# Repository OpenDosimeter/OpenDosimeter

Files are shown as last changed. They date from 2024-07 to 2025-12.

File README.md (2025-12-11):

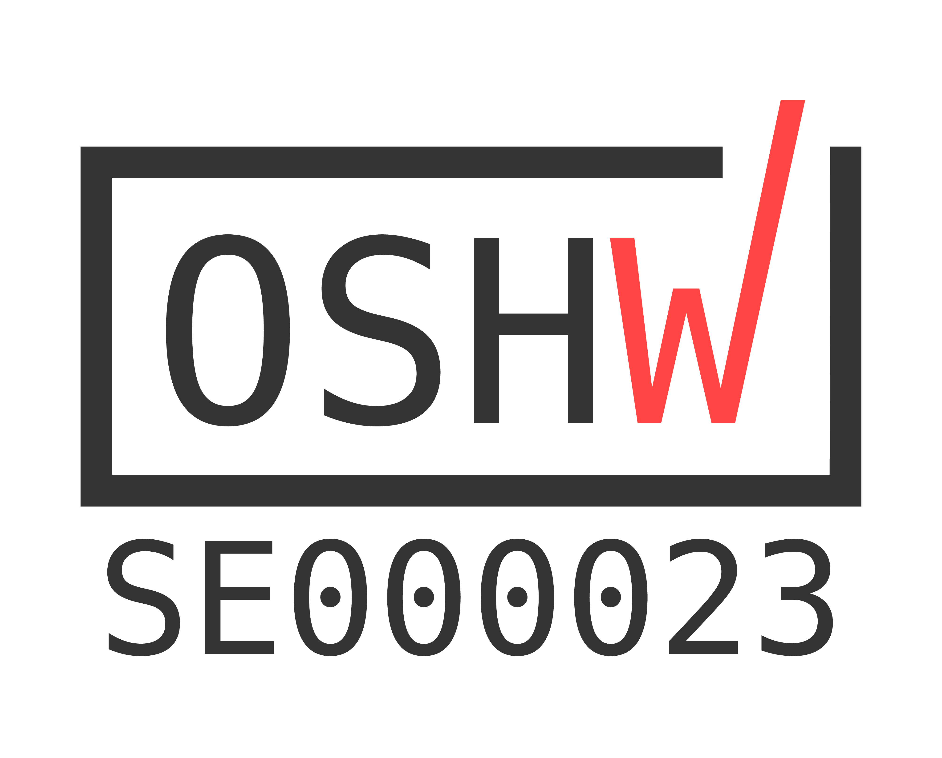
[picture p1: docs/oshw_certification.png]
# OpenDosimeter 

Our open-source hardware and software dosimeter offers an afordable solution for real-time, self-monitored X-ray radiation exposure. With a total component cost of roughly $90, this device provides an accessible option for radiation monitoring to promote broad access to radiation safety. This project is a derivative of the [Open Gamma Detector](https://github.com/OpenGammaProject/Open-Gamma-Detector), with the main new feature being the effective dose calculations (in Sieverts) converted from the detected X-ray spectrum.


<br>
      <blockquote>
        <strong>SAFETY DISCLAIMER:</strong> This is a research project; builders and users assume full responsibility for verifying the accuracy and reliability of measurements obtained from the dosimeters they build. Always follow proper radiation safety protocols and consult with qualified professionals when dealing with radiation exposure.
      </blockquote>
<br clear="both">

<br>

**As of December 1, 2025**, the paper on  OpenDosimeter has been peer reviewed and published in _Communications Engineering_:

<blockquote>

N. Ger, A. Ku, J. Lopez, N. R. Bennett, J. Wang, G. Ateka, E. Anyenda, M. Rosezky, P. Kilavi, A. S. Wang, & K. Shaker, [*"OpenDosimeter: Open hardware personal X-ray dosimeter"*](https://doi.org/10.1038/s44172-025-00540-0) _Commun Eng_ 4, 207 (2025)

</blockquote>

Please cite the paper above if you want to reference the OpenDosimeter project.

## Key Features 

Cost Breakdown

- **Open Design:** Hardware and software designs are fully open-source, enabling reproducibility and customization
- **Affordable:** Total cost ~$90, see [here](https://github.com/OpenDosimeter/OpenDosimeter/tree/main/hardware#table-of-materials) and cost breakdown →
- **Compact:** 73 mm x 42 mm x 23 mm (with the case)
- **Programmable:** Drag and drop firmware files
- **Battery powered:** Current version has a capacity of up to 20 hours per full charge (<70 mA @ at 3.7V, 1200 mAh battery)
- **Accuracy:** Currently reliable between around **0.1 µSv/h to 1 mSv/h** (±25% accuracy) in the [photon counting](https://github.com/OpenDosimeter/OpenDosimeter/blob/main/README.md#working-principle) range
- **Buzzer:** Built in buzzer allows for optional audible warnings when dose rate exceeds predefined limit (default set to 5 µSv/h)
- **Calibratable:** Using Am-241 from any household ionization smoke detector for spectral/dose calibration
- **Real-time:** Direct feedback on radiation exposure, compared to passive dosimeters (e.g., OSL or TLD badges) requiring external readout
- **Logging:** The last 10 hours of dose values are stored on the device; extracted through USB connection and our web interface [here](https://opendosimeter.org/#dataLog)
<br clear="right">

## How to Make One 
**This repository has everything you need to create your own OpenDosimeter:** 

**[Case](https://github.com/OpenDosimeter/OpenDosimeter/tree/main/case):** Use this directory to 3D print the case. It contains two sets of ``.stl`` files that can be downloaded to print top and bottom components for a case with and without a belt clip. 

**[Docs](https://github.com/OpenDosimeter/OpenDosimeter/tree/main/docs):** This is where you can find the reference images used throughout this repository. 

**[Software](https://github.com/OpenDosimeter/OpenDosimeter/tree/main/software):** The software directory has everything you need to program your device, whether you are just looking to download the software with default settings or looking to modify the firmware and make changes to the sketch.  After programming your device, you will be guided through local calibration of your device and an overview of how to use it. 

**[Hardware](https://github.com/OpenDosimeter/OpenDosimeter/tree/main/hardware):** Check out the hardware directory to see the OpenDosimeter board layout in EasyEDA and instructions for ordering it using JLCPCB. This directory contains a breakdown of each component required to assemble the hardware with prices and links to order parts. Furthermore, this is where you can find instructions to assemble your device. 
Additionally, if you prefer to order directly from the PCB manufacturer, you can download the gerber file also located in the ``hardware`` directory or at the [OpenDosimeter Kitspace page](https://kitspace.org/OpenDosimeter/OpenDosimeter).

**[@OpenDosimeter](https://www.youtube.com/channel/UCCUE-LeyRK8Y6H67ti1gdNA):** Finally, head over to our YouTube channel for instructional manuals on ordering the PCB, assembling, programming, and calibrating the device.

## Working Principle 
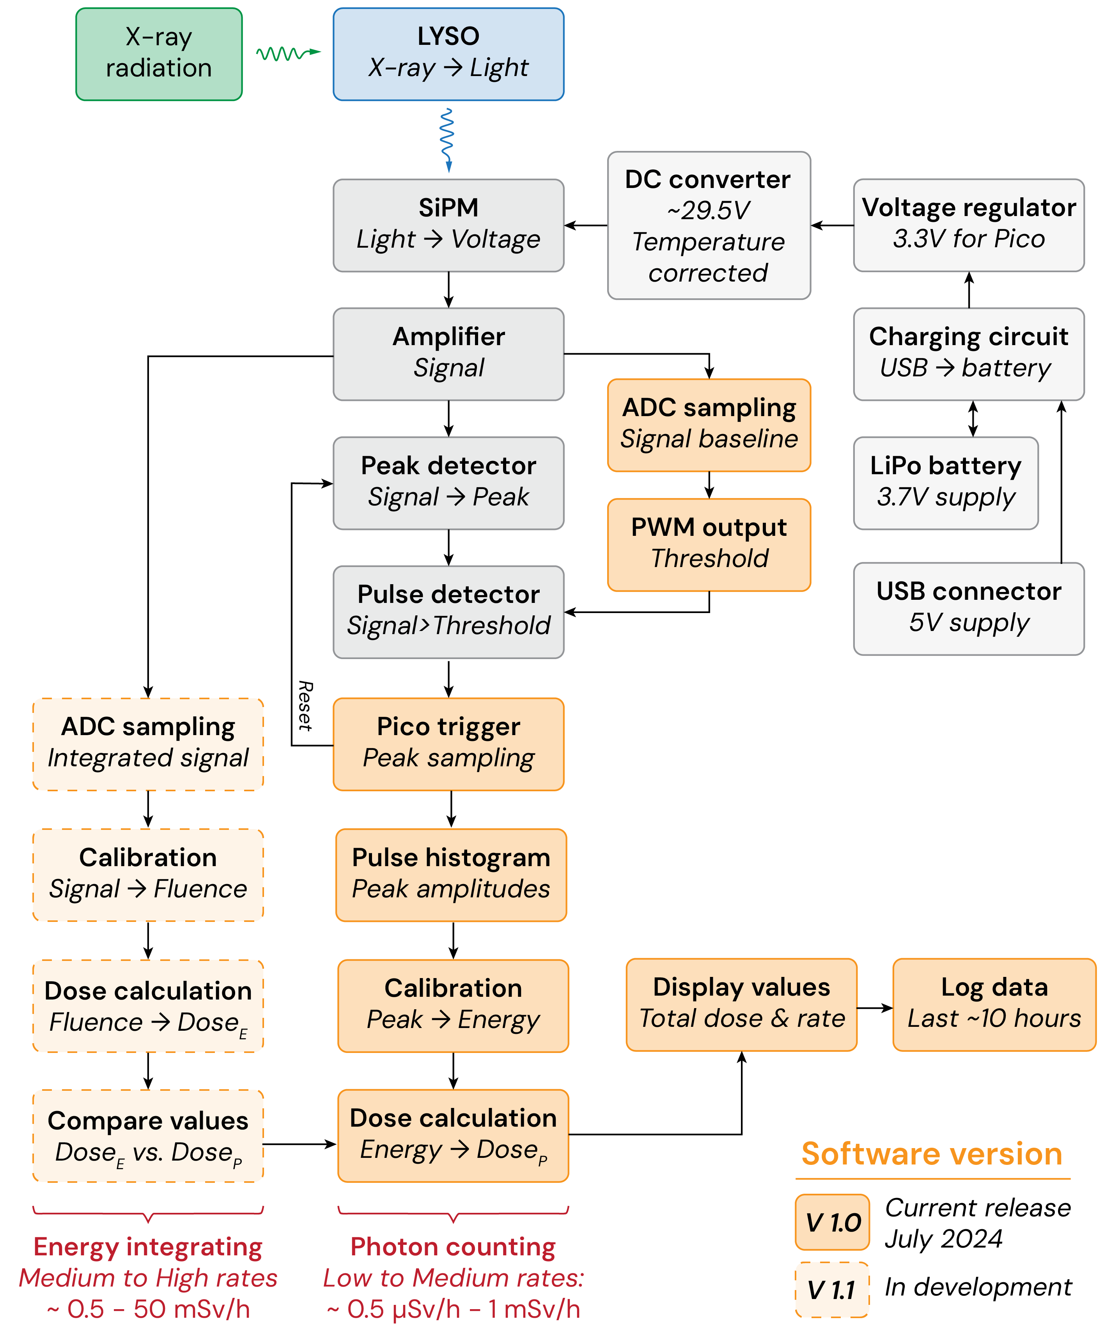
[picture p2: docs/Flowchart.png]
Flowchart of device principle


The flow chart below illustrates the operation, using grey boxes to represent hardware components and orange boxes to indicate software functionality (inspired by the [Open Gamma Detector flowchart](https://github.com/OpenGammaProject/Open-Gamma-Detector/tree/main?tab=readme-ov-file#working-principle), demonstrating the similarity of the underlying design)

The current software (``V.1.0``) converts X-ray photons to dose using a ***photon-counting*** principle (suitable for low to medium dose rates) 

An ***energy-integrating*** parallel component (suitable for medium to high dose rates) is under development for an upcoming software upgrade (``V.1.1``)

<br clear="right">

## Troubleshooting and FAQ
Refer to [REFERENCE.md](https://github.com/OpenDosimeter/OpenDosimeter/blob/main/REFERENCE.md) for troubleshooting support and guidance in debugging

## Future Improvements
1. The current power switch on the OpenDosimeter board is fragile and sometimes breaks. Future iterations of the hardware should replace for a more durable model
2. The power consumption of the current version is quite high (up to 70 mA @ 3.7 V), as it hasn't been optimized for power efficiency. Future hardware and software improvements should be able to improve the power efficiency by at least 2x (i.e., up to 40 hours battery life with a 1200 mAh capacity LiPo).
3. In order to make an even more integrated and compact design, the RP2040 chip from the Raspberry Pi Pico could be incorporated into the OpenDosimeter board 

## Project Team
Many people have contributed to the realization of this project so far:
- Kian Shaker (Stanford University) **[Project lead]**
- Alice Ku (Stanford University)
- Jasmyn Lopez (Stanford University)
- Enoch Anyenda (University of Nairobi)
- Norah Ger (Mama Lucy Kibaki Hospital, Nairobi)
- Grace Ateka (Kenya Bureau of Standards)
- Jia Wang (Stanford University)
- Robert Bennett (Stanford University)
- Adam Wang (Stanford University)
- Matthias Rosezky (https://nuclearphoenix.xyz/)

## Contributing
The OpenDosimeter is a living project and we invite people to contribute to future development!

Want to contribute as a developer? Reach out to [Kian Shaker](https://www.kth.se/profile/kiansd?l=en) (or send an e-mail to opendosimeter@gmail.com)

### Submitting Issues and Suggestions

If you encounter any problems, have questions, or want to suggest improvements:

1. Go to our [Issues page](https://github.com/OpenDosimeter/OpenDosimeter/issues).
2. Click on "New Issue".
4. Provide as much detail as possible about your issue or suggestion.

*Note:* You'll need a GitHub account to submit issues. Another option to leave feedback is to contact us through opendosimeter@gmail.com.

## License

The OpenDosimeter project is released under the GNU General Public License v3.0 (GPL3). This means you're free to use, modify, and distribute the project for any purpose, including commercial applications. However, if you distribute software based on OpenDosimeter, you must make your source code available under the same GPL3 license. This ensures that improvements remain accessible to the community. We encourage innovation and commercial development, as we believe this can lead to wider adoption and further enhancements in radiation safety technology. For the full license text, see the [LICENSE](https://github.com/OpenDosimeter/OpenDosimeter/tree/main?tab=GPL-3.0-1-ov-file) tab in our repository.

## Citation

If your project references OpenDosimeter, or if you use it as a basis for your next cool project, please cite the paper:
<blockquote>

N. Ger, A. Ku, J. Lopez, N. R. Bennett, J. Wang, G. Ateka, E. Anyenda, M. Rosezky, P. Kilavi, A. S. Wang, & K. Shaker, [*"OpenDosimeter: Open hardware personal X-ray dosimeter"*](https://doi.org/10.1038/s44172-025-00540-0) _Commun Eng_ 4, 207 (2025)

</blockquote>

Or directly use the BibTex entry below:

```bibtex
@article{ger2025opendosimeter,
  title={OpenDosimeter: Open hardware personal X-ray dosimeter},
  author={Ger, Norah and Ku, Alice and Lopez, Jasmyn and Bennett, N Robert and Wang, Jia and Ateka, Grace and Anyenda, Enoch and Rosezky, Matthias and Kilavi, Pamela and Wang, Adam S and others},
  journal={Communications Engineering},
  volume={4},
  number={1},
  pages={207},
  year={2025},
  publisher={Nature Publishing Group UK London}
} 

```

## Acknowledgements
_Inspiration:_ The basis for our hardware and software is the fantastic [Open Gamma Detector](https://github.com/OpenGammaProject/Open-Gamma-Detector/tree/main) project, check it out! Much of its detailed documentation is relevant to the OpenDosimeter as well (SiPM behavior, X-ray counting concept etc.)

_Funding support:_ King Center on Global Development at Stanford University, Knut and Alice Wallenberg Foundation (PI: Kian Shaker)

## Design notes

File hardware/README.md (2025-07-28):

# Hardware
Our design leverages the custom OpenDosimeter board with external components including a scintillation crystal (LYSO) coupled to a silicon photomultiplier (SiPM) for X-ray detection, and a Raspberry Pico as for the computation. The board and its components for assembly can also be viewed on [Kitspace](https://kitspace.org/OpenDosimeter/OpenDosimeter). The figure below shows the key features of the OpenDosimeter board. 
<div align=center>
board-overview
</div>

## Components

### OpenDosimeter PCB
Follow these steps to order the OpenDosimeter board (see video instructions below):
1. **Download Files:** download the following files located in this folder
    - [OpenDosimeter_PCB_EasyEDA.json](https://github.com/OpenDosimeter/OpenDosimeter/blob/main/hardware/OpenDosimeter_PCB_EasyEDA.json)
    - [OpenDosimeter_SCH_EasyEDA.json](https://github.com/OpenDosimeter/OpenDosimeter/blob/main/hardware/OpenDosimeter_SCH_EasyEDA.json)
2. **Open in EasyEDA**
    - Go to www.easyeda.com
    - Create an account (or log in if you have one already)
    - Click ``Design Online``
    - Click ``Std Edition``
    - Click ``New Project`` and give it a title
    - Drag and drop both the ``PCB`` and ``SCH`` files into EasyEDA

      | Schematic |Image of Schematic File|
      |---------------------------------------------|--------------------------------------------------------------------------------------|
      | **PCB** |Image of PCB File |

    - ``File`` --> ``Save`` or ``CMD + s`` to save both files to the project you created
    - On the PCB file, click ``Fabrication`` --> ``One Click Order PCB/SMT`` --> ``Yes, Check DCR`` --> ``One Click Order`` --> ``OK``
3. **Open in JLCPCB**
    - Once redirected to JLCPCB, log in or create an account
    - Choose quantity of PCB
    - Recommended: ``Select LeadFree HSL``
    - Select ``PCB Assembly``
    - ``Confirm`` --> ``Next`` --> ``Next`` --> ``OK``
    - Select a product description from drop down
    - Add to cart and checkout
  
**A complete video tutorial for ordering the OpenDosimeter Board is on our YouTube**
<div align="center">
<a href="https://youtu.be/UWabvXynp9I" target="_blank">
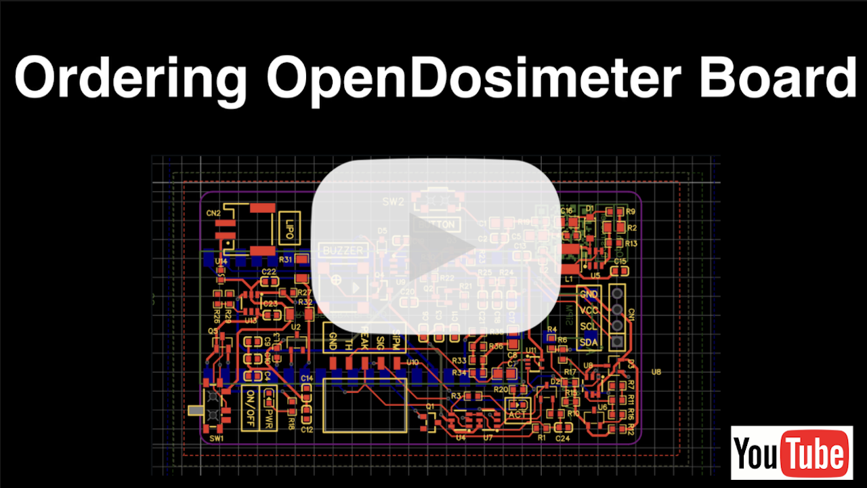
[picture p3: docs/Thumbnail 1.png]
Ordering OpenDosimeter Board Thumbnail
    
</a>
</div>
</br>

### 3D Printed Case 
We have designed a 3D-printable case for the OpenDosimeter. Each case has two parts, a top and bottom. The ``.stl`` files can be found in the [case](https://github.com/OpenDosimeter/OpenDosimeter/tree/main/case) folder.

### Table of Materials
Here are all of the required components and tools for assembly. Also included is the purpose, specification details, cost, and links to purchase each component. 
| Component            | Purpose  | Specification| Cost (USD) | Where to buy (example) |
|------------------------|--------|------------------|------------|---------|
|OpenDosimeter PCB| Main Board  |Custom PCB, see instructions above | $20 |Directly from PCB manufacturer |
|Battery  | Power |LiPo protected battery, ideally >1200 mAh, size around 34mm x 62mm x 5mm | $10 |[1200 mAh Lipo battery](https://www.digikey.com/en/products/detail/adafruit-industries-llc/258/5054544) |
|Display| Displaying dose values to user |128x64 pixels, I2C, SSD1306 | $5 | [Amazon, 128x64 pixels, I2C, SSD1306](https://www.amazon.com/Teyleten-Robot-Display-SSD1306-Raspberry/dp/B0CN373JF4/ref=sr_1_4?crid=2FMQS7B2IFQAD&dib=eyJ2IjoiMSJ9.l-FK2pxw8wWhZ_wtkFb4O1fyrXLIhGQ52dk_-yA7h6FWtEW-CW5RA7_9w5hhpIE9lSkkBIurGV3JAYvQS695jjQR0VVPaO92fd4QVHkD4CTCp4bQsF8CrU8NM0aMPuOZ8RjYMbesVbpG_UDMbMGqyALbXdphIb0nHzBxKLcVF0Pm0UNgyMb1CITVfuh6bqspsPWljCJVLda51Ct931b4NpiFFhTkOtDTzaaWjYwOTCTaZgTjvpziUI1kPpnvJCXBBrgzoC6xlvPtjO4YGGF54xkeJpWnkoouL7rm1iE_GsA.JpSEJVJP5Itir15xcqstihVBHkHDpMhWXXJUSeBi6w4&dib_tag=se&keywords=i2c+128x64+oled+display&qid=1717603122&s=electronics&sprefix=i2c+128x64+oled+sipl%2Celectronics%2C134&sr=1-4) |
|Raspberry Pi Pico| Microcontroller for programming |Regular version with no headers | $4 | [Raspberry Pico](https://www.digikey.com/en/products/detail/raspberry-pi/SC0915/13684020) |
|SiPM| Visible light sensor |6 mm model (MICROFC-60035-SMT-TR) | $33 | [MICROFC-60035-SMT-TR onsemi](https://www.digikey.com/en/products/detail/onsemi/MICROFC-60035-SMT-TR/9742618) |
|LYSO crystal| X-ray to visible light conversion|5x5x1 mm| $30 | [LYSO Ce, 5 x 5 x 1mm](https://www.epic-scintillator.com/LYSO-scintillator-5x5x1mm) |
|Plastic tweezer| Handling LYSO and SiPM | Plastic to prevent scratching the components| $5 |[Amazon, Electronic Repair Plastic Tweezers](https://www.amazon.com/Auniwaig-Anti-static-Tweezers-Precision-Electronics/dp/B08V4BF99K/ref=sr_1_12?crid=2P40DUMKMZHT0&dib=eyJ2IjoiMSJ9.5iYaL1v0I09-iIDQSI0il9h9dCchGEMT1_R94GDH6QmGBH9JFVbAaTAhQZnx0XBo4cjV3EEqDrwTKModIGqUoZWvEqlQyNpFlKvh4ELaqovPHcoU8QCtQ_gAPJ3ZQqBBykfEOf3ee_Jy_4Cu1DA4cSwaO0_pREw9jqP76LslU0dONBOJbGBz6dSRFpDfedrx9rXWLsOMbWLiBONTW1WC0Ly0xX2P2gjgEt74SLqEWsFbY5vmGJeui-m0vcTuJ7wPjrXGSxMzvf9YKbVLzJ0jwkunz39TJtpU8bXlPIO1iSg.wfmLhkznWWSroapnGolqC6t9x1-rZ5mUHo_qM8KZED4&dib_tag=se&keywords=plastic+tweezer+1+pc&qid=1722446225&refinements=p_36%3A-600&rnid=1243644011&sprefix=plastic+tweezer+1+pc%2Caps%2C127&sr=8-12) |
|Electrical Tape| Light sealing of X-ray sensor assembly (SiPM + LYSO) |Black color to efficiently absorb light| $5 |[Amazon, 3/4 Inch Black Electrical Tape ](https://www.amazon.com/Scotch-Super-33-Electrical-carton/dp/B0000AZ9HG/ref=sr_1_3?crid=379MWXWL4Y0R4&dib=eyJ2IjoiMSJ9.XvYh8n8zmezRYWLAeSMp20zS9aMZ_OkZg9vVBnTuU9GBnum6MaLk_FPOJdiiIQndOT6PMejF4weVSVKhDYIE3xq4anvIYIb2bUix0Xf1IJWaM_yuLf7KJLssxgNuyph5Qr31Q8kyOHiXkHE_QoVhGvJzU42l153y9bNqDpVcdg1LXhe9vM8SUbilLvBktT7x3NhoBBvg5GYRCd9G_OwcpAwru3oxciV83fxZaOs_FNA.jo3fPo-i_RRH7EV2clOFCC7W_iUatKs2lCPoXZ7GGuU&dib_tag=se&keywords=electrical+tape+black+3M&qid=1722446293&sprefix=electrical+tape+black+3m%2Caps%2C133&sr=8-3) |
|Aluminum Tape| Light sealing of X-ray sensor assembly (SiPM + LYSO) | Up to 0.1mm thickness to avoid absorbing X-rays | $19 |[Amazon, Aluminum Foil Tape(3M)](https://www.amazon.com/3M-Foil-Tape-3381-Silver/dp/B00A7I5L86/ref=sr_1_4?crid=3FZZ6HXVJFKJW&dib=eyJ2IjoiMSJ9.8g7E604QbHpwyZvpiHS3KOL4D3rbTgkJXTTxyiqD9h9b-tUnIXUthRJ0kzFq5Y0kKPXasQMRFyWgzRdT74c3A0QlN1IbgHV3P2SP6Lm4cNlWMsj0mbBnfrKRNlUb_2VNj8dCcybmoFVXx98mwtjPjzYzJFfLs8Ut27cfT1oYEoi0NeQUm26s7w9ase0wYRub1rl0tQPrTFYCIdzNUsw3XmRI0fHvdR4uIouX2Y2r9mk.iRudZFUJZVLtJbsEUs6dUpkbcNRu_nmlgzl6Sg9rv3g&dib_tag=se&keywords=aluminum+tape+3m&qid=1722446481&sprefix=aluminum+tape+3m%2Caps%2C134&sr=8-4) |
|Optical Couplant | Improving light coupling and adhesion between LYSO crystal and the SiPM  | Should be viscous enough to apply easily, but any will do | $33 | [Amazon, MOLYKOTE 4 Electrical Insulating Compound](https://www.amazon.com/Dow-Corning-Electrical-Insulating-Compound/dp/B0195UWAHG/ref=sr_1_1?crid=1FDS4YSQBHPVO&dib=eyJ2IjoiMSJ9.gfqP0gv9GKU1J2V8zgA0DIDlFhblCyriWhmx9rixKP4DlPxaEkgcBvgK9pTtv9ylH2qXpEG7Q0Jr_dqlBQAYybvFcqWoDgZY5-vvUUvg9PZ8B5LmGmroxZlqPYVmTveAXmyWjn8t2abIkMnV_ef1-QQflucTbNi13fpyZnEI9CO0lSYM9HJYMK2EkayUmpfo-NmrVb7GUy98wMPoeMR1yX3z4wpON1PGkZhy6cWraXs.iPNCpVDAOINZHw5AYk9FiJiEVbZVzLLVk0iQbdBasXg&dib_tag=se&keywords=molykote+4+electrical+insulating+compound&qid=1722446595&sprefix=molykote+in%2Caps%2C131&sr=8-1) |

**Note on Cost**
- Price of the OpenDosimeter board decreases substantially the larger quantity you order (~$20 for a quantity of 15)
- Device assembly only requires small amounts of electrical tape, aluminum tape, and optical couplant, thus the total cost in the table above is inflated by their initial purchase.

## Hardware Assembly

**Follow along instructions for assembling the OpenDosimeter can be found on our YouTube**
<div align="center">
<a href="https://youtu.be/8zaVwqWo00o" target="_blank">
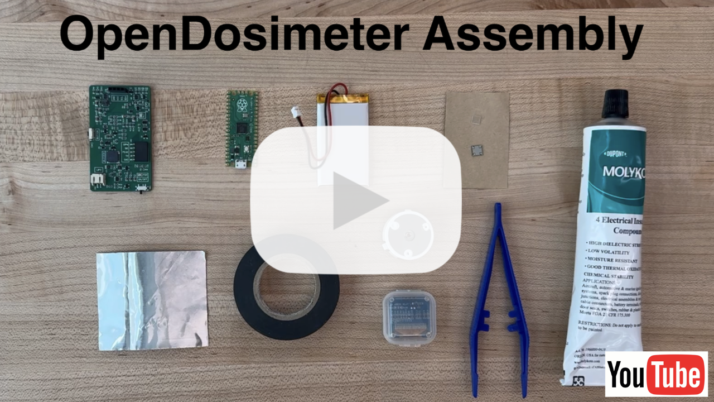
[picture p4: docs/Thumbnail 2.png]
Hardware Assembly Thumbnail
    
</a>
</div>
</br>

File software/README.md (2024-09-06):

# Software 
This software folder contains a precompiled file for simplest set up, and the arduino sketch to make changes to the software. The software was based on the [Open Gamma Detector](https://github.com/OpenGammaProject/Open-Gamma-Detector) (FW. 4.2.1). Below are instructions for how to program your OpenDosimeter once you have assembled it:

## Step 1: Programming the Raspberry Pi Pico
### Option 1: Default Settings
**If you don't want to change the code and just want to program the pico with default settings follow these steps!**
1. Download the [OpenDosimeter_v1.0.1.uf2](https://github.com/OpenDosimeter/OpenDosimeter/blob/main/software/OpenDosimeter_v1.0.uf2) file in the software folder
2. Connect the OpenDosimeter to the computer using the micro-USB port of the Raspberry Pico
3. When it is your first time programming the Pico, it should appear as an external drive. When the  file manager window pops up, drag the ``OpenDosimeter_v1.0.uf2`` file onto the drive. Your device should then automatically restart and is now ready to be calibrated (go to Step 2).
   
**Check out our YouTube video showing the steps above**
<div align="center">
<a href="https://youtu.be/HLWoSg5BW90" target="_blank">
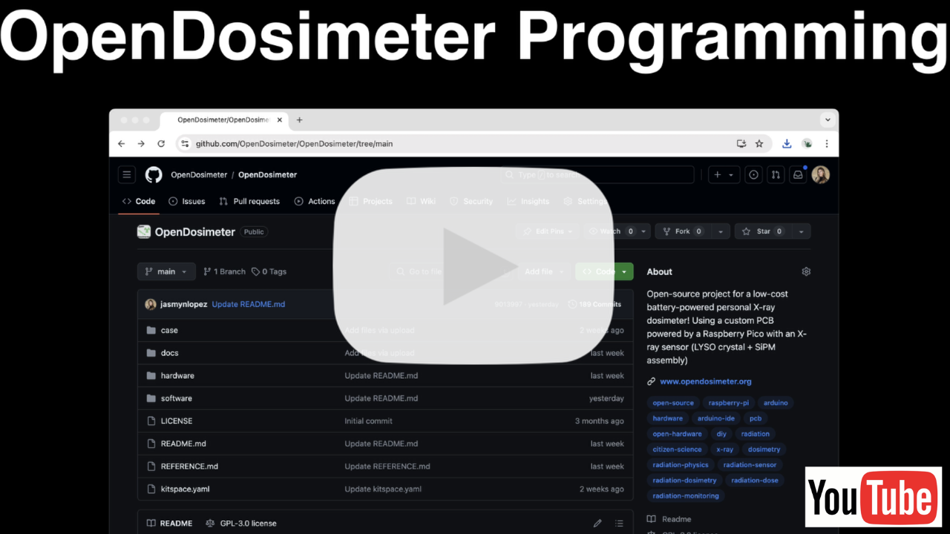
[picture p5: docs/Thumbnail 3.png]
Programming Thumbnail
    
</a>
</div>

### Option 2: Uploading using ArduinoIDE
**Useful if you'd like to see how the code works for potentially modifying it**

_Set up the programming environment_
1. Install ArduinoIDE
2. Install Raspberry Pi Pico Board in the ArduinoIDE
   - Open Arduino --> ``Settings/Preferences`` --> ``Additional Board Managers URL``
   - Add this link: https://github.com/earlephilhower/arduino-pico/releases/download/global/package_rp2040_index.json
   - Press ``OK``
   - Go to ``Board Manager``
   - Search for "Raspberry Pico" and install ``Raspberry Pi Pico/RP2040 by Earle F. Phillhower, III``
        - **NOTE**: Make sure the installed version is 3.9.5 (newer versions cause problems, as of Aug 30, 2024)
3. Use the Library Manager (``tools`` --> ``library manager)`` to install the following dependency packages
    - ``TaskScheduler``
    - ``SimpleShell Enhanced``
    - ``ArduinoJson``
    - ``Adafruit_SSD1306``
    - ``Adafruit_SH110X``
    - ``RunningMedian``
    - ``RunningAverage``

_Download the OpenDosimeter software_

4. Download the .zip [OpenDosimeter_v1.0.1.zip](https://github.com/OpenDosimeter/OpenDosimeter/tree/main/software/OpenDosimeter_v1.0.1.zip) which contains the .ino source code
5. Open the file ``OpenDosimeter_v1.0.1.ino`` to open the code in ArduinoIDE
6. Here you can inspect and modify the code to add new desired features
   
_Program the Device_

8. Flash the Pico
    - Connect Pico over USB
    - Choose the following settings:
       - **Board:** ``Tools`` --> ``Board`` --> ``Raspberry Pi RP2040 Boards``
       - **Port:** ``Tools`` --> ``Port`` Select associated port 
       - **Flash Size:** ``Tools`` --> ``Flash Size: 2MB (Sketch: 1MB, FS: 1MB)``
    - Keep remaining settings at default values
    - Press the ``Upload`` button

## Step 2: Calibrating the Device
**A step-by-step guide for calibrating the device is on our YouTube channel**
<div align="center">
<a href="https://youtu.be/eI6PJFmvRmY" target="_blank">
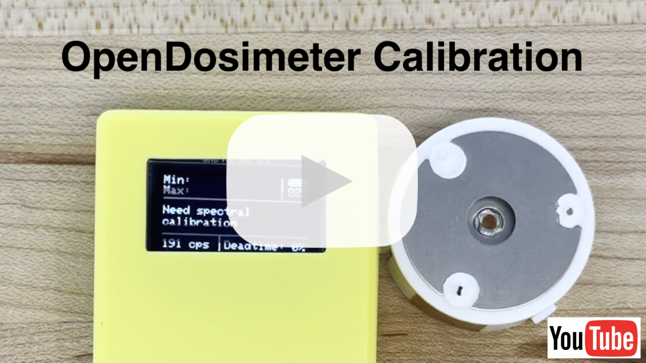
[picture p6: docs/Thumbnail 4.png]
Calibrating Thumbnail
    
</a>
</div>
</br>

1. Extract Am-241 from any household ionization smoke detector
    - See this [video](https://www.youtube.com/watch?v=lOWNI6bC5EM) for disassembling instructions
2. Turn ``ON`` your assembled and programmed device (using the power switch)
3. ``Long Press`` side button to open Reset/Calibration menu
4. ``Long Press`` again to begin calibration
5. Align Am-241 with the circle on the back of the case
    - You should see two peaks forming
    - Keep Am-241 in place until calibration is complete (up to 1 minute recording)
6. Your device should say ``Calibrating...Done``

**For troubleshooting, checkout the [REFERENCE.md](https://github.com/OpenDosimeter/OpenDosimeter/blob/main/REFERENCE.md)**

## Step 3: Programmed Device Overview
**A complete overview of the device is on our YouTube channel**
<div align="center">
<a href="https://youtu.be/77HooAmk0_8" target="_blank">
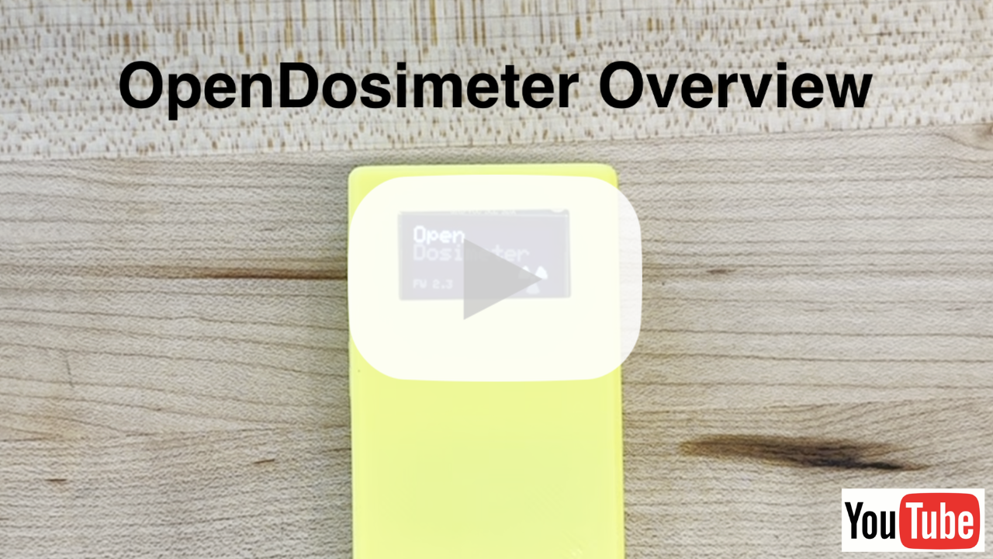
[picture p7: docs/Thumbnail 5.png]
Device Overview Thumbnail
    
</a>
</div>
</br>

Once your device is programmed, you should see the OpenDosimeter home screen and firmware version. Below is a flowchart that shows how you can use the side button to navigate between the different programmed states. 
<div align="center">
software states
</div>

## Data Log Generation
This [web interface](https://opendosimeter.org/#dataLog) allows makers of OpenDosimeter to connect their device through USB, then visualize the stored dose log (past 10 hours) with the options to download the data as a .csv file for further analysis.

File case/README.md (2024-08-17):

The case (enclosure) for the OpenDosimeter has been designed using [Onshape](https://www.onshape.com/en/), a free CAD program in the web browser.

The .STL files here can be downloaded for 3D printing using any 3D printer with accompanying slicer.

For access to the design files in Onshape, see here:  [OpenDosimeter case (top + bottom)](https://cad.onshape.com/documents/6fcbce0a05899a100007238a/w/146bfa9a71857ea974a3a549/e/9a98d43933894009a95632ed?renderMode=0&uiState=66c112a07b1c1b2b1835d26e) 



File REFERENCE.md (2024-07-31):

# Troubleshooting and FAQ 

## Troubleshooting 

#### Calibration/Device Settings are Not Saved 
This is likely due to not allocating any memory for the file system. When you flash the Pico, be sure that you have selected the following setting: ``Boards`` --> ``Flash Size: 2MB (Sketch: 1MB, FS: 1MB)`` so the Pico has memory allocated for the file system. 

#### Calibration is failing 

## FAQ 

#### Can I Modify the Program? 
Yes! Check out Step 1, Option 2 in the software [README.md](https://github.com/OpenDosimeter/OpenDosimeter/blob/main/software/README.md) for detailed instructions to modify the code and flash the Pico using ArduinoIDE.

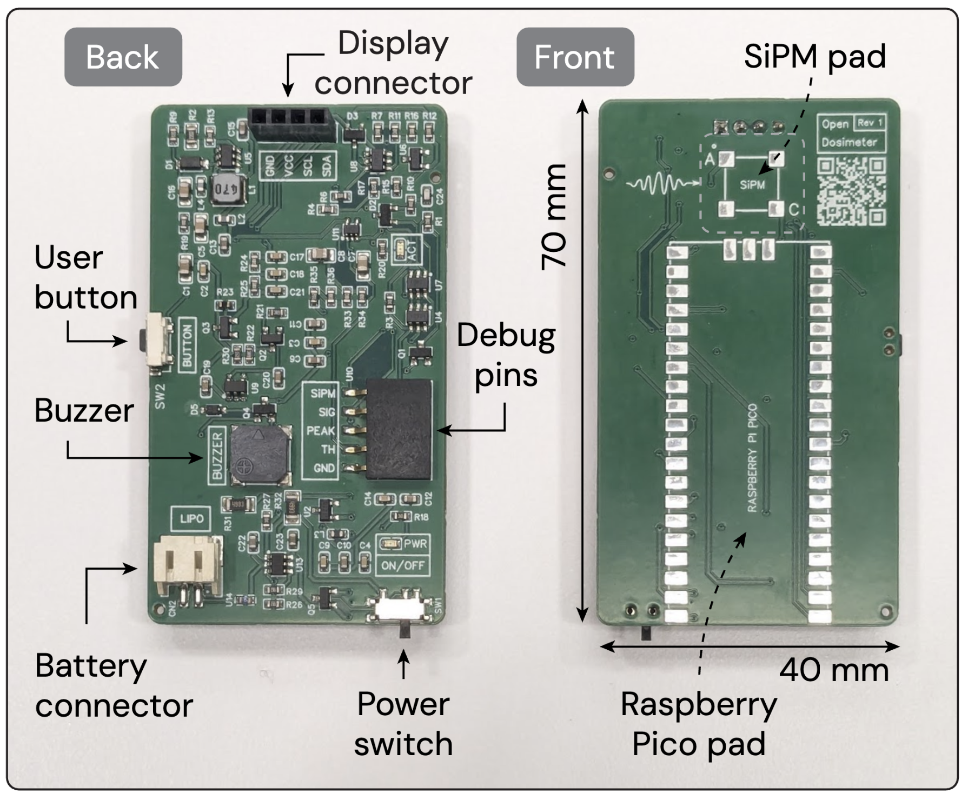
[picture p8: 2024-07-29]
docs/device-overview.jpg

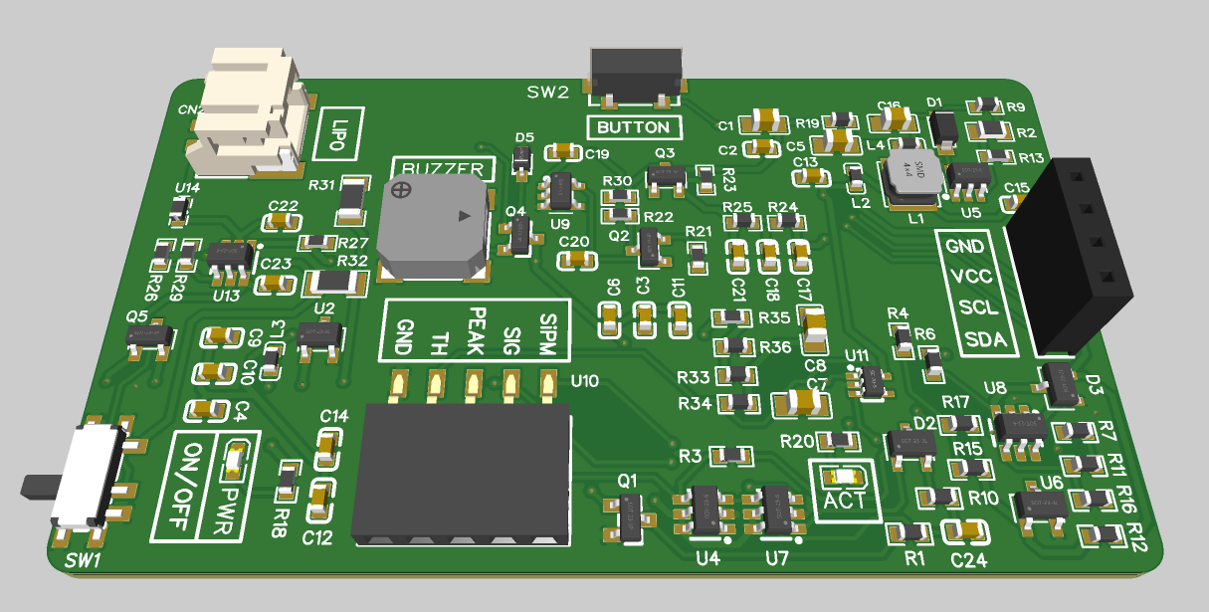
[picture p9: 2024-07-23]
docs/Board 3D rendering, top.png

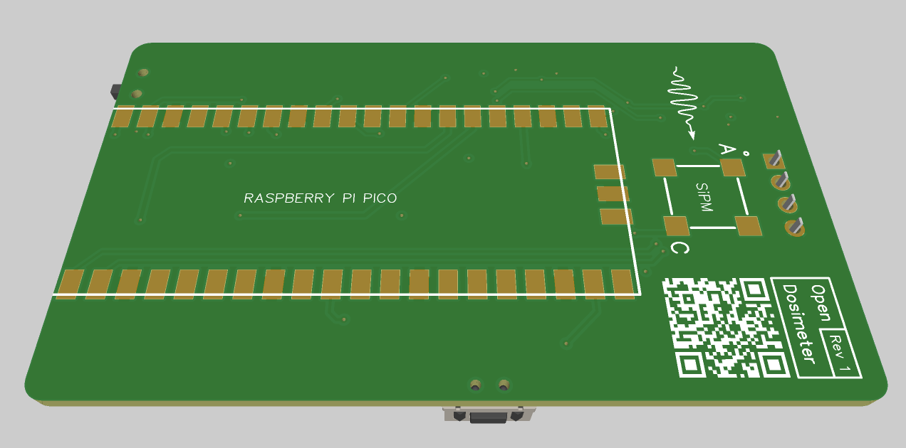
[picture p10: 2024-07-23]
docs/Board 3D rendering, bottom.png

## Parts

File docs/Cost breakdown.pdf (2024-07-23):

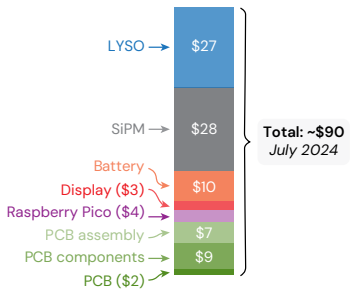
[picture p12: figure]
LYSO; SiPM; Total: ~$90; July 2024; Battery Display ($3) Raspberry Pico ($4) PCB assembly PCB components PCB ($2)

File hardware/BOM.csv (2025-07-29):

ID | Name | Designator | Footprint | Quantity | Manufacturer Part | Manufacturer | Supplier | Supplier Part | Price | Pins | Contributor | JLCPCB Part Class | Resistance | Resistance (Ohms) | link
1 | LTST-C190KGKT | ACT,PWR | LED0603-RD | 2 | LTST-C190KGKT | LITEON(光宝) | LCSC | C125094 | 0.014 | 2 | LCSC | Extended Part
2 | SMD-7525-3627-16Ω | BUZZER | BUZ-SMD_4P-L7.5-W7.5-BR | 1 | SMD-7525-3627-16Ω | S&S(海旭) | LCSC | C2685546 | 0.27 | 4 | LCSC | Extended Part |  |  | https://lcsc.com/eda_search?q=C2685546&%26type=1&ref=editor
3 | 4.7uF | C1,C5,C16 | C0805 | 3 | CL21A475KBQNNNE | SAMSUNG(三星) | LCSC | C98192 | 0.02 | 2 |  | Extended Part
4 | 100nF | C2,C3,C4,C9,C14,C17,C18,C21 | C0603 | 8 | CL10B104KB8NNNC | SAMSUNG(三星) | LCSC | C1591 | 0.002 | 2 |  | Extended Part
5 | 10uF | C6,C10,C11,C12,C13,C15,C22,C23 | C0603 | 8 | CL10A106MQ8NNNC | SAMSUNG(三星) | LCSC | C1691 | 0.004 | 2 |  | Extended Part
6 | 47uF | C7,C8 | C0805 | 2 | CL21A476MQYNNNE | SAMSUNG(三星) | LCSC | C16780 | 0.024 | 2 |  | Basic Part
7 | 2.2uF | C19,C20 | C0603 | 2 | CL10A225KB8NNNC | SAMSUNG(三星) | LCSC | C913904 | 0.02 | 2 | LCSC | Extended Part
8 | 470pF | C24 | C0603 | 1 | CC0603JRNPO9BN471 | YAGEO(国巨) | LCSC | C106211 | 0.004 | 2 |  | Extended Part |  |  | https://lcsc.com/eda_search?q=C106211&%26type=1&ref=editor
9 | 2.54-1*4P母 | CN1 | HDR-TH_4P-P2.54-V-F | 1 | 2.54-1*4P母 | BOOMELE(博穆精密) | LCSC | C2718488 | 0.041 | 4 | LCSC | Extended Part
10 | HC-PH-2AWT | CN2 | CONN-SMD_PH-2AWT | 1 | HC-PH-2AWT | HCTL(华灿天禄) | LCSC | C2845442 | 0.044 | 4 | LCSC | Extended Part
11 | PMEG4010CEGWJ | D1 | SOD-123_L2.7-W1.6-LS3.6-RD | 1 | PMEG4010CEGWJ | Nexperia(安世) | LCSC | C552899 | 0.062 | 2 | LCSC | Extended Part
12 | BAT54S,215 | D2,D3 | SOT-23-3_L3.0-W1.7-P0.95-LS2.9-BR | 2 | BAT54S,215 | Nexperia(安世) | LCSC | C47546 | 0.011 | 3 |  | Extended Part
13 | SiPM | D4 | MICROFC−60035−SMT | 1 | MICROFC-60035-SMT-TR1 | ON Semiconductor | Mouser | 863-MFC60035SMTTR1 |  | 3 | Gamma_001 |  |  |  | https://www.mouser.at/datasheet/2/308/MICROC-SERIES-D-1489614.pdf
14 | PMEG4010BEA | D5 | SOD-323_L1.8-W1.3-LS2.5-RD | 1 | PMEG4010BEA,115 | Nexperia(安世) | LCSC | C36975 | 0.038 | 2 |  | Extended Part
15 | 47uH | L1 | IND-SMD_L4.0-W4.0 | 1 | SPH4018H470MT | Sunlord(顺络) | LCSC | C98405 | 0.072 | 2 |  | Extended Part
16 | 1kΩ | L2,L3,L4 | L0603 | 3 | BLM18KG102SN1D | muRata(村田) | LCSC | C160982 | 0.015 | 2 | LCSC | Extended Part
17 | 2N7002,215 | Q1,Q4 | SOT-23_L2.9-W1.3-P1.90-LS2.4-BR | 2 | 2N7002,215 | Nexperia(安世) | LCSC | C65189 | 0.018 | 3 |  | Extended Part
18 | MMBT5088LT1G | Q2,Q3 | SOT-23-3_L2.9-W1.3-P1.90-LS2.4-BR | 2 | MMBT5088LT1G | onsemi(安森美) | LCSC | C232555 | 0.046 | 3 | LCSC | Extended Part
19 | DMG2305UX-13 | Q5 | SOT-23-3_L2.9-W1.3-P1.90-LS2.4-BR | 1 | DMG2305UX-13 | DIODES(美台) | LCSC | C144153 | 0.066 | 3 | LCSC | Extended Part |  |  | https://lcsc.com/eda_search?q=C144153&%26type=1&ref=editor
20 | 1kΩ | R1,R4,R7,R11,R12,R16,R33,R34,R36 | R0603 | 9 | 0603WAF1001T5E | UNI-ROYAL(厚声) | LCSC | C21190 | 0.001 | 2 |  | Basic Part |  | 1K
21 | 22kΩ | R2 | R0805 | 1 | 0805W8F2202T5E | UNI-ROYAL(厚声) | LCSC | C17560 | 0.002 | 2 |  | Basic Part
22 | 10kΩ | R3,R13,R18,R27 | R0603 | 4 | 0603WAF1002T5E | UNI-ROYAL(厚声) | LCSC | C25804 | 0.001 | 2 |  | Basic Part |  | 10K
23 | 100Ω | R6,R10,R19 | R0603 | 3 | 0603WAF1000T5E | UNI-ROYAL(厚声) | LCSC | C22775 | 0.001 | 2 |  | Basic Part |  | 100
24 | 210kΩ | R9,R15,R17 | R0603 | 3 | 0603WAF2103T5E | UNI-ROYAL(厚声) | LCSC | C22952 | 0.001 | 2 |  | Extended Part |  | 210K
25 | 1kΩ | R20 | R0603 | 1 | ARG03BTC1001 | Viking(光颉) | LCSC | C309080 | 0.018 | 2 | LCSC | Extended Part |  |  | https://lcsc.com/eda_search?q=C309080&%26type=1&ref=editor
26 | 49.9kΩ | R21,R22 | R0603 | 2 | RT0603BRD0749K9L | YAGEO(国巨) | LCSC | C705780 | 0.022 | 2 | LCSC | Extended Part | 49.9kΩ
27 | 10KΩ (NTC) | R23 | R0603 | 1 | NTCS0603E3103FLT | VISHAY(威世) | LCSC | C142556 | 0.381 | 2 | LCSC | Extended Part
28 | 49.9Ω | R24,R25 | R0603 | 2 | 0603WAF499JT5E | UNI-ROYAL(厚声) | LCSC | C23185 | 0.001 | 2 |  | Basic Part |  | 49.9
29 | 1.8kΩ | R26,R29 | R0603 | 2 | 0603WAF1801T5E | UNI-ROYAL(厚声) | LCSC | C4177 | 0.001 | 2 |  | Basic Part |  |  | https://lcsc.com/eda_search?q=C4177&%26type=1&ref=editor
30 | 24kΩ | R30 | R0603 | 1 | 0603WAF2402T5E | UNI-ROYAL(厚声) | LCSC | C23352 | 0.001 | 2 |  | Basic Part |  |  | https://lcsc.com/eda_search?q=C23352&%26type=1&ref=editor
31 | 499kΩ | R31,R32 | R1206 | 2 | AR06FTD4993 | Viking(光颉) | LCSC | C304140 | 0.012 | 2 | LCSC | Extended Part
32 | 5.6kΩ | R35 | R0603 | 1 | 0603WAF5601T5E | UNI-ROYAL(厚声) | LCSC | C23189 | 0.001 | 2 |  | Basic Part
33 | SK-3296S-01-L3 | SW1 | SW-SMD_SK-3296S-01-L3 | 1 | SK-3296S-01-L3 | XKB Connectivity(中国星坤) | LCSC | C319019 | 0.074 | 4 | LCSC | Extended Part |  |  | https://lcsc.com/eda_search?q=C319019&%26type=1&ref=editor
34 | TS36CA-0.6 250GF 031 | SW2 | SW-SMD_SHOU_TS36CA-0.6 | 1 | TS36CA-0.6 250gf 031 | SHOU HAN(首韩) | LCSC | C2906288 | 0.022 | 4 | LCSC | Extended Part
35 | LM4040AIM3-3.0+T | U2,U6 | SOT-23-3_L2.9-W1.6-P1.90-LS2.8-BR | 2 | LM4040AIM3-3.0+T | MAXIM(美信) | LCSC | C143326 | 1.52 | 3 | LCSC | Extended Part
36 | PI-PICO-SMD | U3 | RASPBERRY PICO SMD | 1 | PICO | Raspberry Pi | LCSC | C7203002 | 6.327 | 43 | MicroRobotics
37 | OPA357AIDBVR | U4,U7,U8 | SOT-23-6_L2.9-W1.6-P0.95-LS2.8-BR | 3 | OPA357AIDBVR | TI(德州仪器) | LCSC | C139385 | 1.049 | 6 | LCSC | Extended Part
38 | MAX5026EUT+T | U5 | SOT-23-6_L2.9-W1.6-P0.95-LS2.8-BL | 1 | MAX5026EUT+T | MAXIM(美信) | LCSC | C87603 | 1.565 | 6 | LCSC | Extended Part
39 | TPS7B6950DBVR | U9 | SOT-23-5_L3.0-W1.7-P0.95-LS2.8-BL | 1 | TPS7B6950DBVR | TI(德州仪器) | LCSC | C174327 | 0.433 | 5 | LCSC | Extended Part
40 | X6511FRS-05-C85D30 | U10 | HDR-SMD_5P-P2.54-H-F_X6511FRS-19-C85D30 | 1 | X6511FRS-05-C85D30 | XKB Connectivity(中国星坤) | LCSC | C5142238 | 0.17 | 5 | lcsc | Extended Part
41 | TLV3201AIDCKR | U11 | SC-70-5_L2.1-W1.3-P0.65-LS2.1-TL | 1 | TLV3201AIDCKR | TI(德州仪器) | LCSC | C130037 | 0.684 | 5 | LCSC | Extended Part
42 | BQ21040DBVR | U13 | SOT-23-6_L2.9-W1.6-P0.95-LS2.8-BR | 1 | BQ21040DBVR | TI(德州仪器) | LCSC | C202311 | 0.3 | 6 | LCSC | Extended Part |  |  | https://lcsc.com/eda_search?q=C202311&%26type=1&ref=editor
43 | 06D0750D | U14 | F0603 | 1 | 06D0750D | LANSON(良胜) | LCSC | C182438 | 0.052 | 2 | LCSC | Extended Part

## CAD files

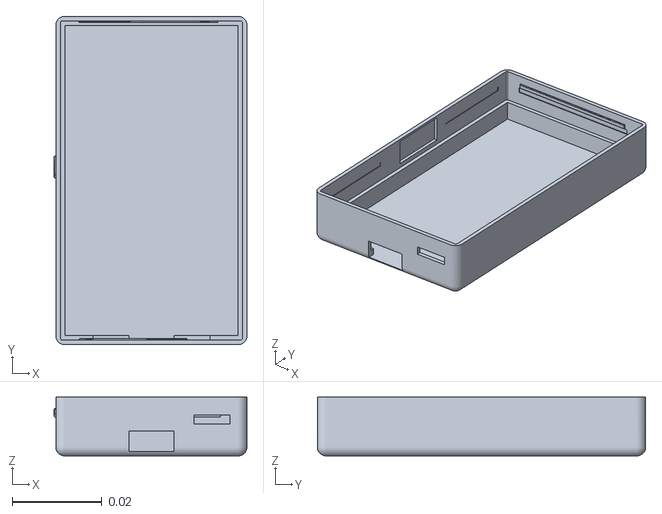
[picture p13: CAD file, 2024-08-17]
case/Case (bottom).stl
0.0429 x 0.073 x 0.0131

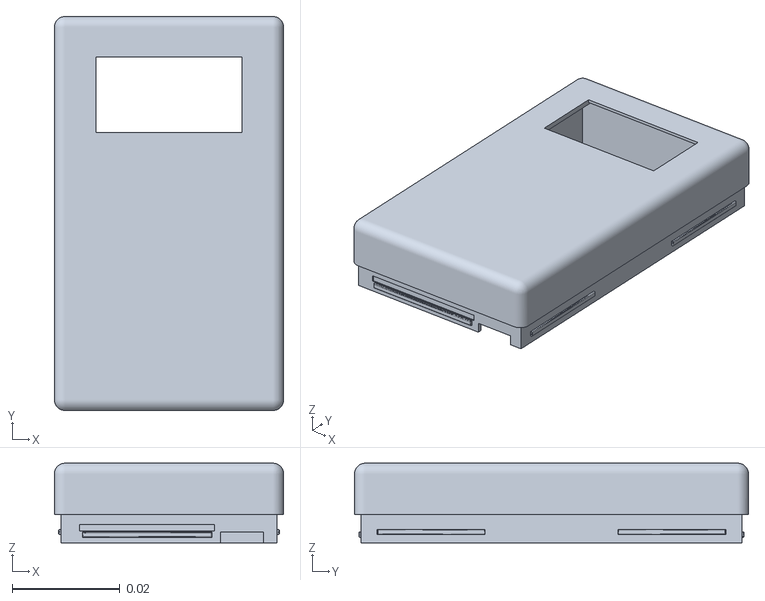
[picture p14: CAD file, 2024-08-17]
case/Case (top).stl
0.0425 x 0.073 x 0.0148

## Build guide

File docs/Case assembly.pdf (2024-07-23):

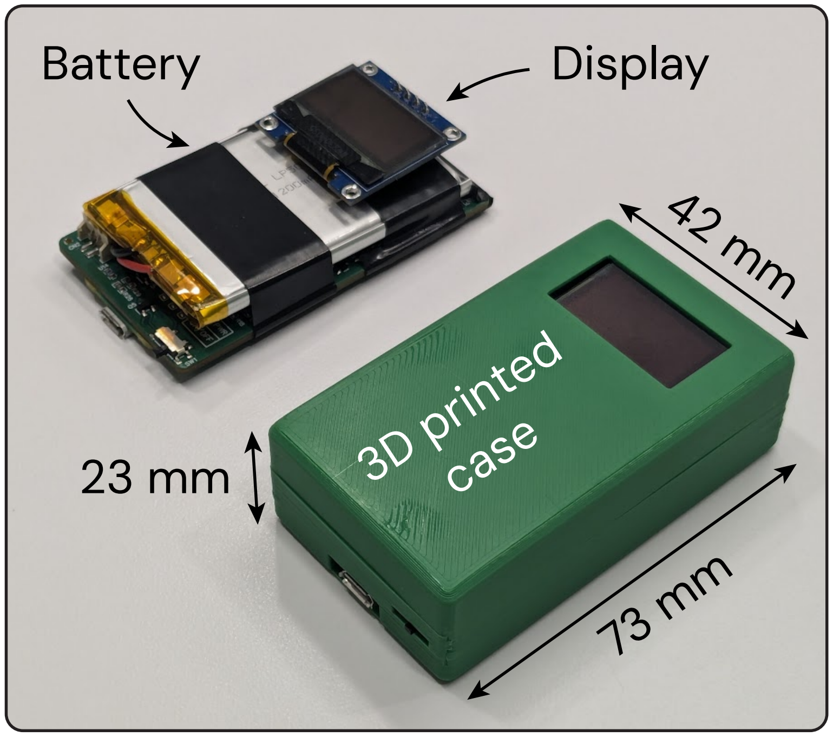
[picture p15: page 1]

Battery

3D printed
case

Display

42 mm

73 mm

23 mm

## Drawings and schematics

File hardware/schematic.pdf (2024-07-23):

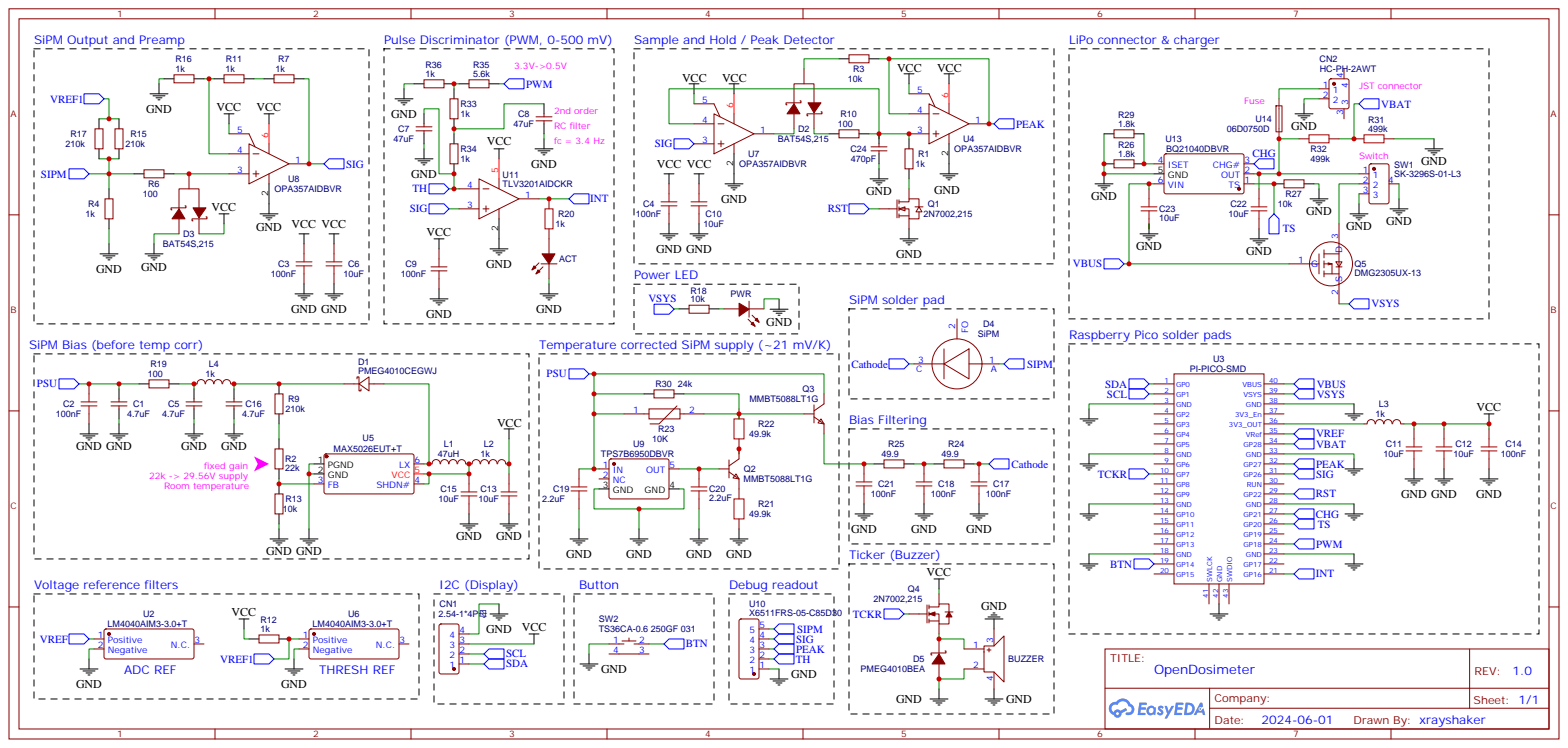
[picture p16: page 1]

SiPM Output and Preamp

Pulse Discriminator (PWM, 0-500 mV)

Sample and Hold / Peak Detector

Raspberry Pico solder pads

SiPM Bias (before temp corr)

Temperature corrected SiPM supply (~21 mV/K)

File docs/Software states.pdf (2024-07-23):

## Accumulated dose

0.03

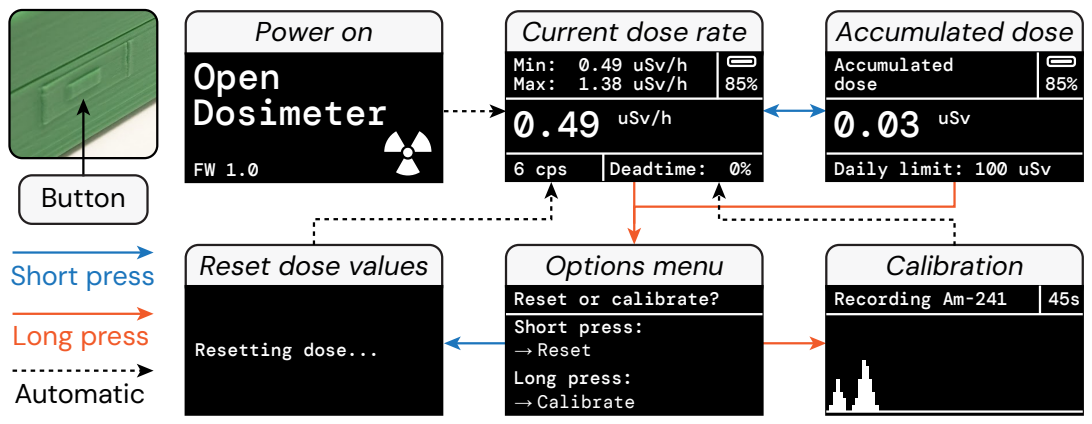
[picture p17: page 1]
Accumulated dose; uSv; Button; 6 cps; Deadtime: 0%; uSv/h; Power on; Open Dosimeter; Calibration; Recording Am-241; Short press

Current dose rate
Min: 0.49 uSv/h
Max: 1.38 uSv/h

Daily limit: 100 uSv

Reset dose values

Options menu
Reset or calibrate?
Short press:
→ Reset
Long press:
→ Calibrate

Resetting dose... Long press
Automatic

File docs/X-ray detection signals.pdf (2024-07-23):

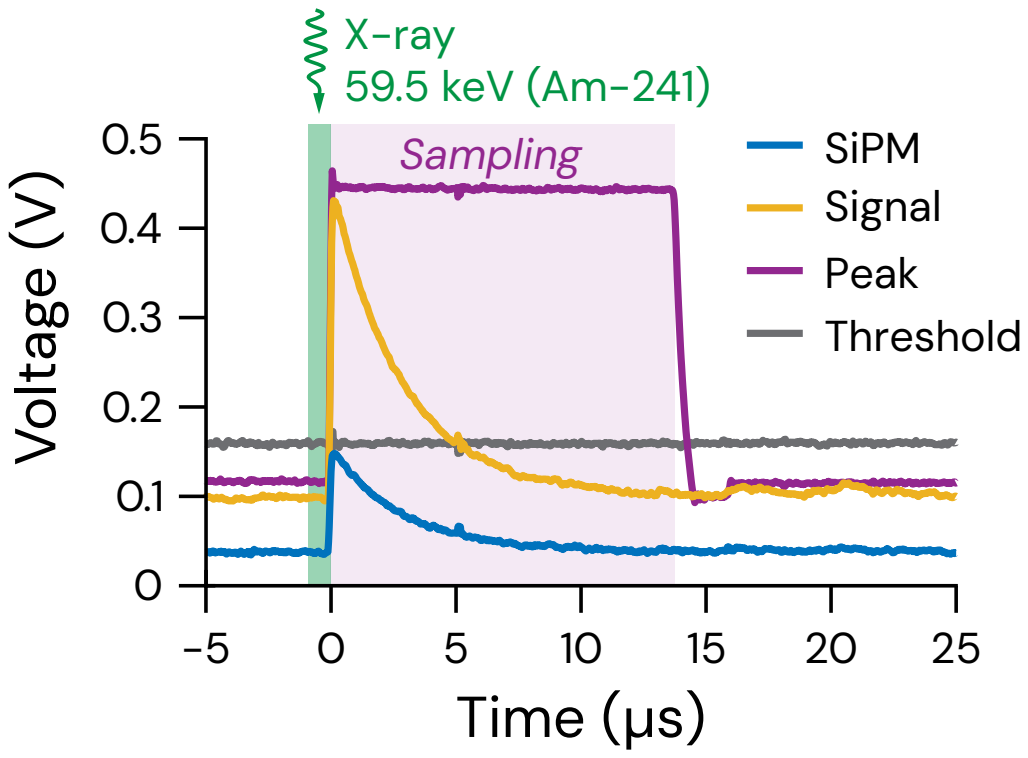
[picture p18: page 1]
SiPM; X-ray 59.5 keV (Am-241); Signal Peak; Sampling; Threshold; Time (µs); Voltage (V)

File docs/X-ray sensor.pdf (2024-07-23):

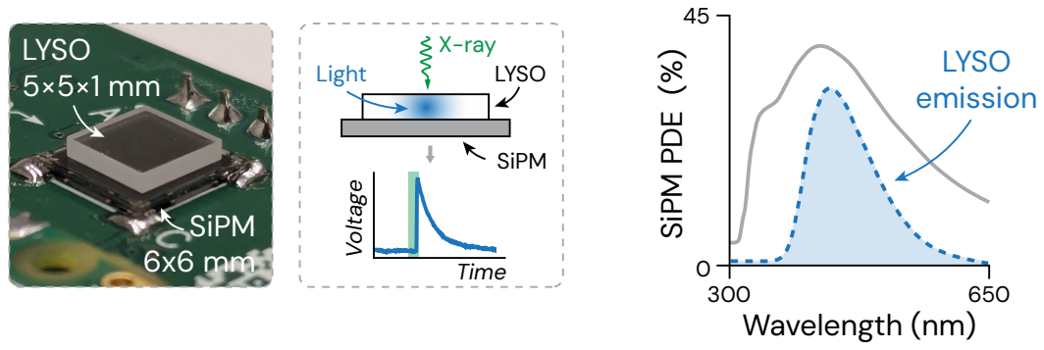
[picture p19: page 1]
LYSO 5×5×1 mm; SiPM 6x6 mm; LYSO emission; SiPM PDE (%); Wavelength (nm); Light; LYSO; X-ray; SiPM; Time; Voltage

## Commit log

2024-08-17 Rename Bottom.stl to Case (bottom).stl
    [Case (bottom).stl]
2024-08-17 Rename Top.stl to Case (top).stl
    [Case (top).stl]
2025-02-14 Fixup BOM.csv
    [BOM.csv]
2025-07-21 Update BOM.csv
    Possible fix to Issue #5, adding a [NTC] flag to R23 to have Kitspace separate it into it's own entry row.
    [BOM.csv]
2025-07-26 Corrected a spelling mistake: 'Recomended' → 'Recommended'
2025-07-29 Separated R23 10k NTC resistor (for Kitspace IBOM)
    Added a (NTC) flag to the R23 resistor so that it appears separately in the Kitspace IBOM assembly viewer.
